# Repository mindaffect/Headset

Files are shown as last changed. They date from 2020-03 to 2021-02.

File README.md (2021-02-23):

# Headset
Here you can find:
- Initial print files of the headset based on TMSi waterbased electrodes (4 channels + ref + ground). You can find a quick tutorial on https://youtu.be/Aez5LA2C2G4 of V1.0 made by Nikolai Schauer. Please read the printing guide before trying to print. 
- Instructions on how to set up the MindAffect headset
- Information on lay out when not supplied with a MindAffect headset

# Support

If you run into issues, either raise  an issue directly on github, or contact the developers on [gitter](https://gitter.im/mindaffect) -- to complain,complement or just chat.

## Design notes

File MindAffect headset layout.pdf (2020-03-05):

Headset layout MindAffect cVep system
Brain-Computer Interfaces (BCIs) allow users to control devices and communicate by using brain activity only. BCIs based on broad-band visual stimulation can outperform BCIs using other stimulation paradigms. Visual stimulation with pseudo-random bit-sequences evokes specific code-modulated Visual Evoked Potentials (cVEPs) that can be reliably used in BCI for high-speed communication in, for example, speller applications.

The typical response to code-modulated Visual Evoked Potential Brain Computer Interfacing is strongest in the locations as shown below, where the blue spot has the significant activation.

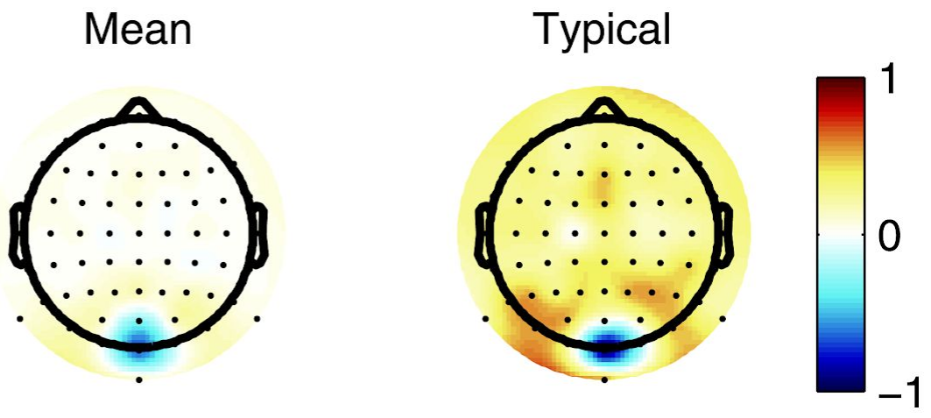
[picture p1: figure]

https://doi.org/10.1371/journal.pone.0133797

Our headset is designed such that the bottom electrode is just above the inion, the bump on the back of your head right above the neck. The electrodes are spaced exactly 4cm apart, this distance is based on extensive data analysis of acquired EEG signals. The headset used by MindAffect contains water-based electrodes with AgCl. However, we believe it should work with typical cup-electrodes or dry electrodes when the connections are made right.

MindAffect headset
For the Ganglion we only use 4 working electrodes, located in a row approximately 1cm above the inion. They are centered around the reference electrode in the middle (median/sagittal plane), which leads to two electrodes on the left and two on the right of the reference electrode. The ground is mounted on the forehead by a conducting headband, however, one can use an electrode sticker on the forehead, a bracelet around the wrist or use an electrode as far away as possible from the brain signals measured.

MarkIV UltraCortex headset
The OpenBCI headset has successfully been tested with the use of the O1, Oz, Poz and O2 electrodes for the signals, the Pz for the reference and one of the earclips for the Ground. Please note that only a handful of tests have been conducted with this headset, and the electrodes might not be optimal. Also, note that the headset is made of dry electrodes, this might induce longer classification times.

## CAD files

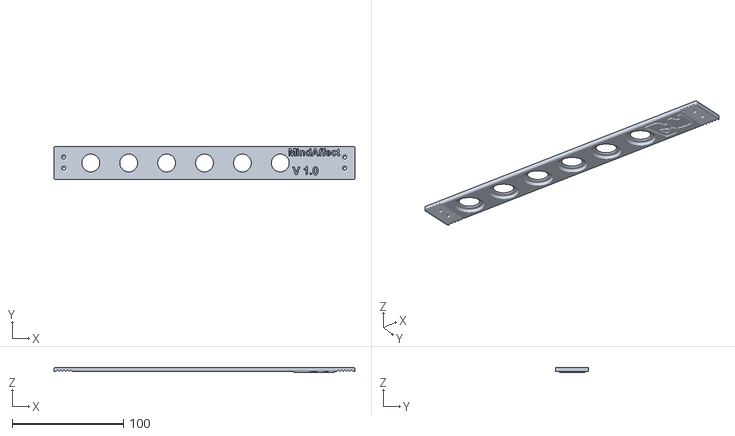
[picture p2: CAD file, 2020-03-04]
Main-Part.stl
270.0 x 30.0 x 4.20

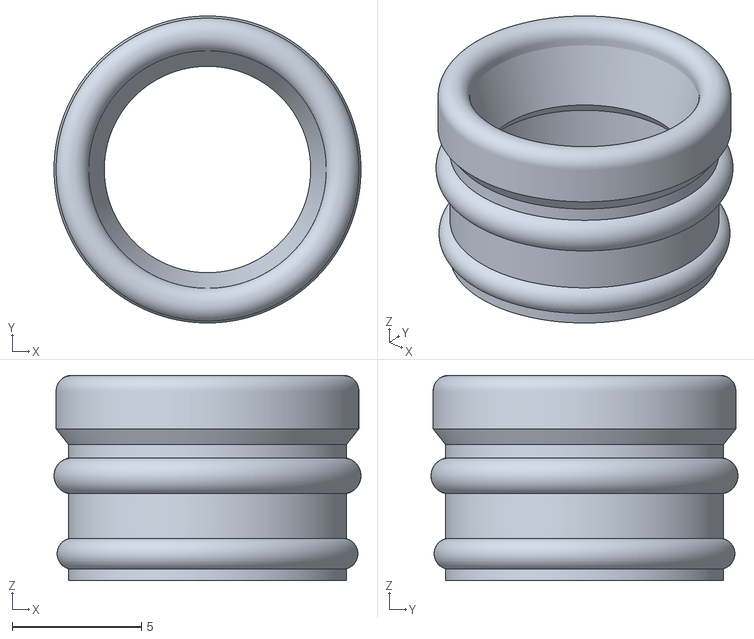
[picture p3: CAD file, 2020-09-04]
Files for integrated electrodes/sponge_holder.stl
11.9 x 11.9 x 7.93

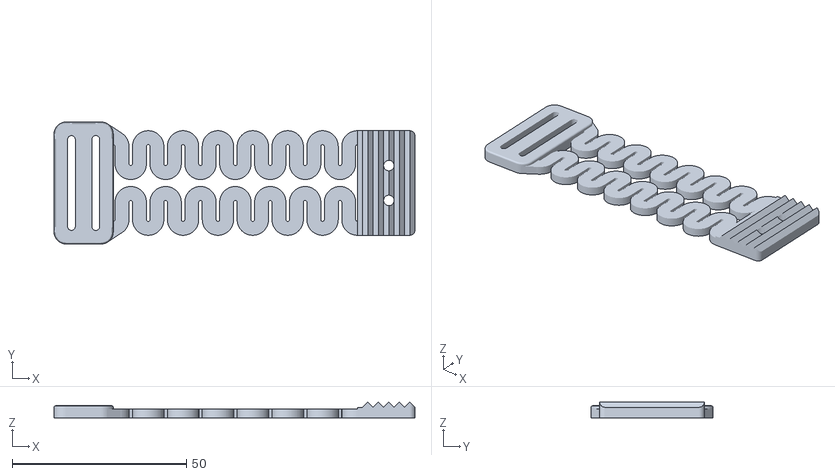
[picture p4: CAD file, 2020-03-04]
Attachment.stl
103.5 x 35.0 x 4.55

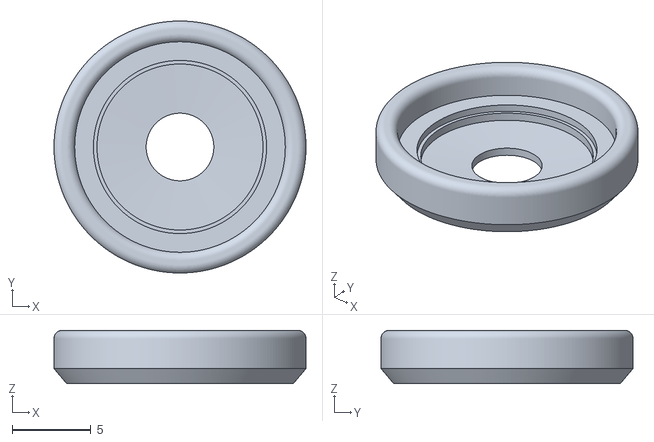
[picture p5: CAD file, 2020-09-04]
Files for integrated electrodes/disc_holder.stl
16.0 x 16.0 x 3.40

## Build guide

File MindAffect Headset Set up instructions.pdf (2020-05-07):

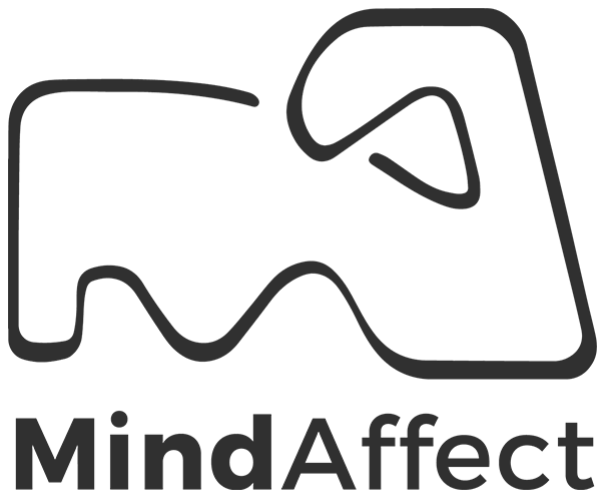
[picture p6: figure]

### 2. Setup headset

### 2.1 Prepare headset

1. Get a glass of water
2. Fill the plastic syringe with water
3. Roll the sponges to fit into the headset
4. Put the sponges in the electrode cups in the
headset.
5. Wet the sponges from the top with the syringe with water. Make sure to fill them until they are saturated. This can be detected when water doesn't get absorbed by the sponges anymore.
1) 2)

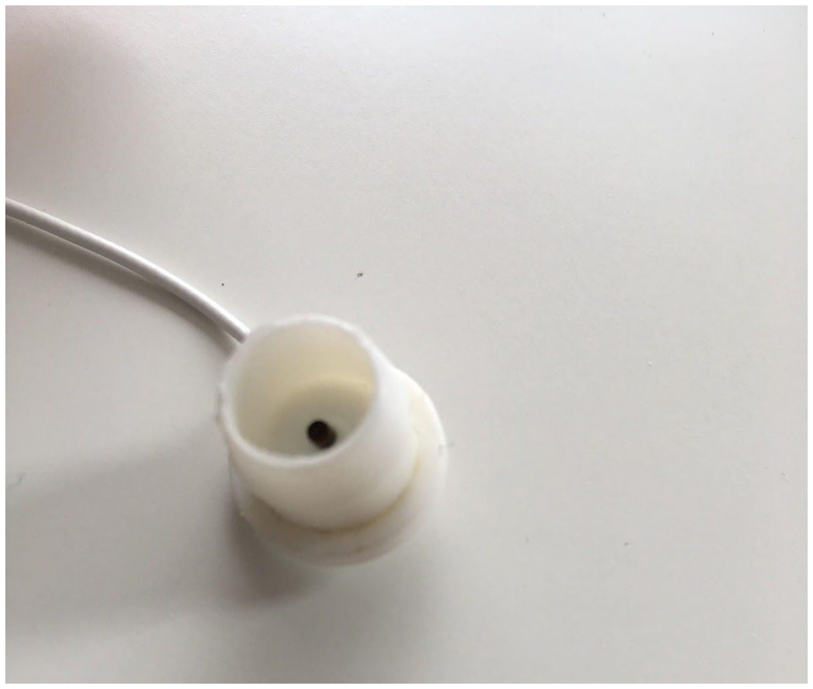
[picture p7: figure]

3)

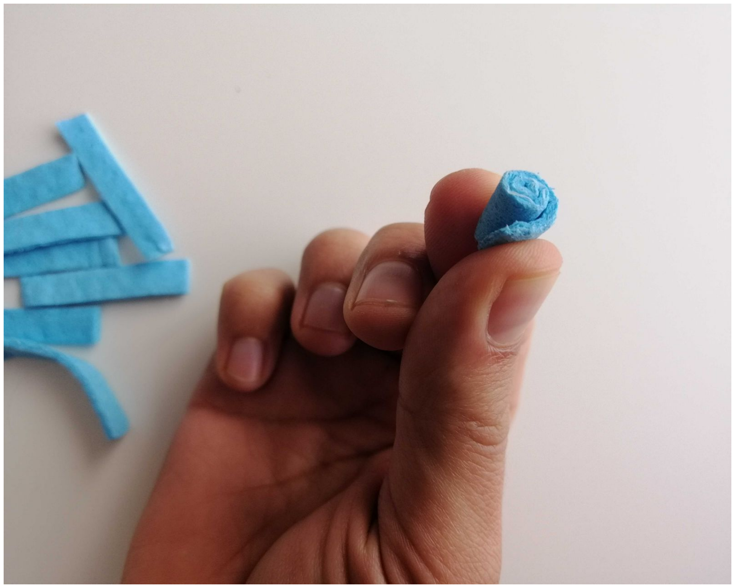
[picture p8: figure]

1

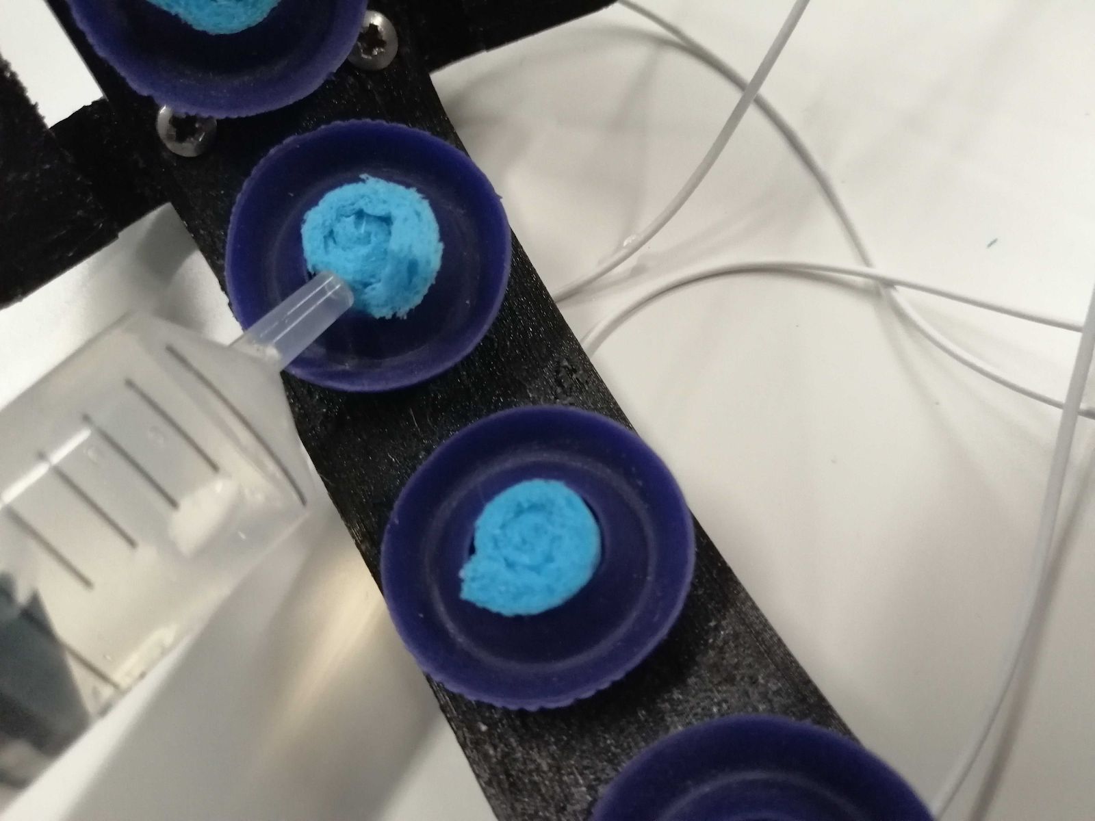
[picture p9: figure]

### 2.2 Place headset

Before positioning the headset on the user’s head, inspect it to see if there are no
damaged parts that might hurt the user. Please remove any metal parts in the hair (hair clips, ornaments, etc). Please notes that the picture on the left contains an older version of the headset. The newer versions have the logo displayed on the left instead of the outer left electrode in the images.
When using the system with several users or
when the headset has become soiled, you can

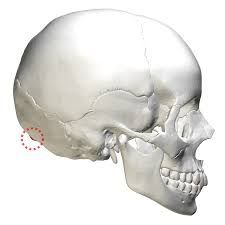
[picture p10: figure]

clean the headset using a moistened (by water) cloth. Do not use detergents, as this might damage the electrodes.

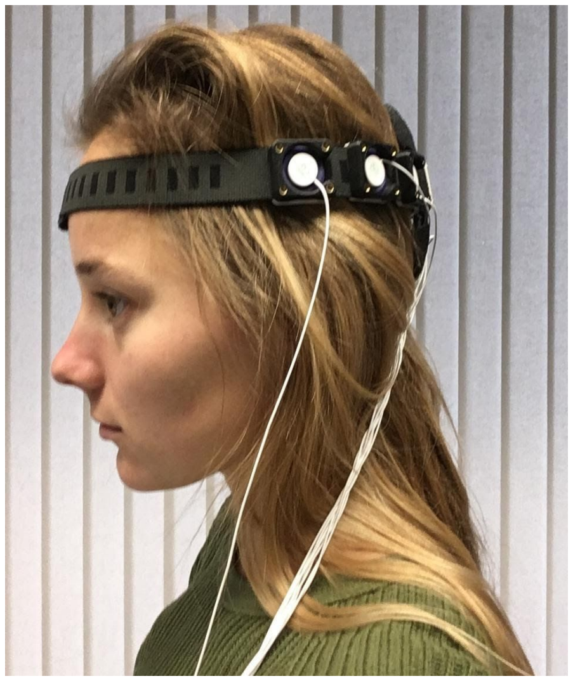
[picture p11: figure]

The headset needs to be placed directly above the inion (a small protrusion at the back of the skull).

1. Put the hard part of the headset on the back of the head with the electrode cables facing downwards (see image on the left upper corner).
2. Tighten the strap on the front of the head to make sure the headset stays in place (not too tight that it gets uncomfortable).
3. Press all electrodes carefully on the head by pressing the white circle plates. The participant must feel it is wet.
4. If the cables were disconnected from the green connector plate, please connect the cables to the right number displayed next to the plugs on the green connector
5. Connect the connector to the OpenBCI amplifier with ‘BCI top’ test facing upwards (such that channel 2,4 and ground are facing upwards as well).

2

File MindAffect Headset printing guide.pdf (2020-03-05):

# MindAffect Headset printing guide

Per headset, 3 pieces need to be printed:
1x Main-Part.stl
2x Attachment.stl

We recommend semi-flexible filament, but anything flexible should work. Stiff material like PLA, PETG or ABS won’t work!
We used “Renkforce Flexible Filament” for all prototypes.

We recommend these print settings:

Nozzle: 0.4 mm
Extrusionwidth: 0.5mm
Layerheight: 0.25mm
Brim: 3mm
Speed: 20mm/s
Infill: 40% (This value can be adjusted to compensate for more flexible filament; a higher infill value will make for a more stiff headset)
Perimeters: 5
Bottom layers: 5
Top layers: 5

Temperature: See filament spool

The print settings are of course dependent on your personal printer and will most likely require some tuning.

The parts were designed to fit on most buildplates, in some cases “Main-Part.stl” needs to be rotated by a few degrees (Prusa MK3 for example).
